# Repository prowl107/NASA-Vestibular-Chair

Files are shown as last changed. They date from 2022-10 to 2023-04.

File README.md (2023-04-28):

# NASA-Vestibular-Chair
This project is designed with the goal of restoring the NASA Vestibular Chair. The chair was actively involved in research at NASA and was recently acquired by Embry-Riddle Aeronautical University faculty. This involves restoring the basic functionality and then adding software functionality to improve the ease of use.

## Vision Statement
Our goal for the end of the spring semester (2023) is to accurately introduce a web-based interface into the external controller along with defining more accurate data acquisition over wireless connection. This consists of encoding a Raspberry Pi to allow for communication of testing procedure specifications to the microcontroller opposed to having manual input. The data acquisition will be achieved through the use of Bluetooth modules present in the microcontroller to communicate data to a host console wirelessly. If time permits, we would begin refining and updating the current design of the external controller for better usability and aesthetic. 

## Installation
```bash
git clone git@github.com:prowl107/NASA-Vestibular-Chair.git
cd NASA-Vestibular-Chair
git config user.name "User"
git config user.email "admin@example.com"
```
Alternatively, you can use a git GUI client to manage your copy of the project. 

## Usage
Open Visual Studio Code (or your text editor/IDE of choice) and then open the PlatformIO menu.
Select "Open Project" and navigate to where the repo is located on your device.
Open the PlatformIO project with the NASA-Vestibular-Chair root folder selected.
Have fun :)

## Hardware 
### Version 1 - Controller Module
| Category  | Component  |
|---|---|
| MCU  |  [Arduino Mega 2560 Rev3](https://store.arduino.cc/products/arduino-mega-2560-rev3) |
| Motor Controller  | [Pololu Simple Motor Controller G2 24v12](https://www.pololu.com/product/1365)  |
| Display  | [Standard 20x4 LCD w/ I2C](https://www.amazon.com/SunFounder-Serial-Module-Arduino-Mega2560/dp/B01GPUMP9C) |
| I/O  | SPST Momentary switch; 250k potentiometer  |
| Power Supply | USB 5v |
| Communication Interface (Receiver) | [433Mhz Receiver](https://www.amazon.com/HiLetgo-Wireless-Transmitter-Receiver-Raspberry/dp/B01DKC2EY4/ref=sr_1_3?keywords=433mhz+transmitter+and+receiver&qid=1675643344&sr=8-3) |

**NOTE:** Initially, the plan was to utilize a [Nucleo-WB55RG](https://www.st.com/en/evaluation-tools/nucleo-wb55rg.html) Development board. Due to time constraints and availability, the Arduino Mega (and Nano) were chosen due to their extensive library/peripheral support and quick prototyping capabilitiy.

### Version 1 - Patient Remote

| Category  |  Component |
|---|---|
| MCU  | [Arduno Nano R3](https://store.arduino.cc/products/arduino-nano)  |
| I/O  |  3x SPST Momentary switch |
| Power Supply   | 5v li-ion battery  |
| Communication Interface (Transmitter)  |  [433Mhz Receiver](https://www.amazon.com/HiLetgo-Wireless-Transmitter-Receiver-Raspberry/dp/B01DKC2EY4/ref=sr_1_3?keywords=433mhz+transmitter+and+receiver&qid=1675643344&sr=8-3) |

## Presentations
- [Sprint 1 Demo Presentation](https://docs.google.com/presentation/d/1b5IdnyLSNwiTLVy-gZ9E79ZbYqnyJbTD/edit?usp=sharing&ouid=115407868332019012098&rtpof=true&sd=true)
- [Sprint 2 Demo Presentation](https://docs.google.com/presentation/d/1l_CmvSCrBEOVg_VuYpDZWNs5qSBOpJvT/edit?usp=sharing&ouid=115407868332019012098&rtpof=true&sd=true)
- [Sprint 3 (End of Fall 2022) Demo Presentation](https://docs.google.com/presentation/d/1xmUZu0XUEXimdjX_mnKVwzS-KKVoy4oE/edit?usp=sharing&ouid=115407868332019012098&rtpof=true&sd=true)
- [Sprint 4 (2023) Demo Presentation](https://docs.google.com/presentation/d/1zxAWRcQLVy_wj2OVS8DIGSSmD8TUqGN_/edit?usp=sharing&ouid=115407868332019012098&rtpof=true&sd=true)
- [Sprint 5 (2023) Demo Presentation](https://docs.google.com/presentation/d/1c0bh65YAwqH6N8ktK_QlXqYoBvHQKnEx/edit?usp=sharing&ouid=115407868332019012098&rtpof=true&sd=true)
- [Final Presentation](https://docs.google.com/presentation/d/1rVZELndvWFqBjD3BzsnxDw-WVZXjoCnKRoX8ANc6Zlw/edit?usp=sharing)

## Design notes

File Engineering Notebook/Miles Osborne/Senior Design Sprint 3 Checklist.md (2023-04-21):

Web Interface Integration
Final Presentation
- New theme (ask Carson)
- System architecture
SRS updates
SDS updates
- Mostly just diagrams and software artifacts
- intended fully wireless design
Documentation:
- User manual
PCB
- Prototype with breadboards and intended power supply
- That needs to be finished post haste
3D printed enclosure
Move to fully wireless?
Fixing data logger
Test tachometer in lab on thursday/friday

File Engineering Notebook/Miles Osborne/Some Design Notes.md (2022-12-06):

# Some Design Notes

## Use Case

### Actors
- Patient
- Proctor
- Web Interface
- Chair 
- Controller module

### Responsibilities:

#### Patient Responsibilities:
- Sit in the chair
- Indicate what direction they are spinning in
- Activate soft switch

#### Proctor Responsibilities: 
- Start test sequence
- Activate soft switch
- Activate mechanical/hard switch
- Control RPM via switch

#### Web Interface Responsibilities
- Display data 
- Accept commands from I/O

#### Chair Responsibilites
	Send data
		- Accelerometer
		- Tach

#### Controller Module
- Process commands
- Read data over serial
- Send sign

### Assumptions:
- Assuming that the controller module consists of the following components:
	- Micro controller
	- Motor controller
	- 1x soft switch
	- 1x hard switch
	- 7 seg displays

### Constraints:

## State Transitions (For the chair-controller interaction)

- Powering off
	- Entry: Kill voltage to system if powered
	- Leave state once mechanical switch is pressed/depressed
	- Can go back to powering on state, once kill switch is not enabled

- Powering on
	- Entry: System initialization
	- exit: nothing
	- Do: Cycle displays 
	- Leave state once system initialization completes

- Configuring sequence
	- Nested state
	- 1. Configuring RPM
		- Leave after center pushbutton confirmation
		- Stay in state if down button is pressed 
	- 2. Configuring Time/Duration
		- Leave after centeR pushbutton confirmation
		- Go back to previous state if down button is pressed

- Waiting for proctor confirmation
	- Enter if test sequence has been set and confirmed
	- DO: Wait
	- Exit: nothing
	- Only leave state once proctor gives pushbutton confirmation
	- Go back to configuring sequence if down button is pressed

- Executing test sequence
	- Do: Send signals to chair via motor controller
	- Only enter state if arming switch is triggered

- Slowing down
	- Enter this state if soft_kill switch is pressed at any point
	- Do: Quickly bring RPM down to 0
	-

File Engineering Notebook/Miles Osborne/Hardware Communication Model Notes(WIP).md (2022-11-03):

# Hardware Communication Model Sections:
## 1. Controller Interfaces
- STM32 MCU
- Dedicated motor controller
- Dial/potentiometer to control RPM manually
- Switch to arm/comfirm ready for test
- Soft kill switch
- Buffer to store data
- 2x 7 Segment displays
- Hard kill switch
## 2. NASA Vestibular Chair
- Soft kill switch for patient
- Accelerometer
- Tach 
- Servo motor
  - Part that spins the chair
- User joystick
  
## 3. Displays and outgoing data
- Web interface

## 4. Incoming signals

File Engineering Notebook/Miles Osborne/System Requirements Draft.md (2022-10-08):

# System Requirements Draft

# Control
- The system shall allow the chair to spin upto a specified RPM
- After a specified duration set by the operator/proctor, the chair should enter a free coast state
- The system should allow the chair to spin in either clockwise or counterclockwise directions
- The system shall have a "soft" kill switch that will allow the chair to "free coast" down to 0 rpm
- The system shall have a "mechanical/hard" kill switch that will bring the chair to stop faster than the soft switch
	- By how much faster?
- The system should adjust `<parameter>` in response to the user's weight in order to maintain the desired RPM
	- Not sure what parameter needs to be adjusted yet (voltage, current, etc...)

- **HOW DOES THE RPM GET SET**?
- The system shall not exceed `<parameter>` RPM at any point during its operation

- Do not exceed 10v power consumption
- DO not exceed 4a power consumption
# Web Interface
The system shall have a web interface that allows the user/proctor to control the following

- The web interface shall allow the operator to add different test sequences 
	- **NOTE:** We don't know what constitutes a test sequence entirely yet
- The web interface shall allow the proctor to input the user's weight
- The web interface shall feature a unique button to select the test sequence
- The web interface shall have a unique button to start the selected test sequence
- The web interface shall have a text box to enter the duration of the test 
- The web interface shall display stored test sequences from a dropdown menu

# Data Acquisition
- The system shall record chair steady state (current position) of the chair
- The system shall record the rpm set by the proctor
- The system shall record the rpm that the chair is currently spinning at
	- NOTE: We will need an encoder for this
- The system shall record the time elapsed during the current test
- When the user indicates they are spinning, the system shall record the total time the user thinks they are spinning 
- When the user thinks they are spinning, the system shall record the direction they think they are spinning in 
- When the user thinks they are spinning, the system shall record the timestamps they think they are spinning for
- The system shall have the ability to export data in a human readable formate
	- Something like excel, csv, json, etc.
- The system shall have the ability to obtain positional data from an external accelerometer

# User Input/Feedback
- The system shall support user input from a bi-directional control interface
	- Button, joystick, etc.
- The system shall allow for the user to indicate what direction they are spinning in via a bi-directional control method
- The proctor cannot start a sequence or test until a separate button/switch is pressed
- The system shall record intermediate values for the direction indicated
	- x (slow, medium, fast) amount in left direction
	- x (slow, medium, fast) amount in right direction
- The user remote is wireless
- Controller has wireless recieve and transmit functionality

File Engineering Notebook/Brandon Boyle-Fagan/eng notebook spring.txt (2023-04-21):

1/11/23 - Meet with team to go over tasks and important deadlines for upcoming sprint. Compiled list of requirements to make part box container.

1/14/23 - Started modeling designs for controller box. includes power supply, arduino, motor controller, I/O

1/18/23 - Printing designs for controller box.

1/20/23 - Printing desing for controller box and assembly.

1/21/23 - Assemble first controller box. test and deug motor controller box with MAtthaeus, and Miles, as well as test first implementation of wireless remote.

1/22/23 - More 3D printing.
 
1/23/23 - Moved chair to HAL. Tested that the controller box work to power chair. assembled and soldered circuit for wireless remote.

1/26/23 - Worked with Dylan on creating a base to read the data from the tachometer 

1/27/23 - talked to Dr. Garcia about ways to Read the data from the potentiometer

2/16/23 - Talked to Dr.Pang on way to implement a PID based control system into the chair and tachometer feedback system. Worked with Dylan to Update the tachometer to use new measurement system. 

2/23/2023 - Attempted to reinstall Tach into chair.

2/27/2023 - Redesigned and printed the new casing design  for the paitent remote control.

3/3/23 - Worked in HAL to attach tachometer to chair. 

3/7/23 - Worked in HAL along with Miles and Kent to attach tachometer to chair and get RPM data from it. 

3/28/23 - class discussion to go over project

3/30/23 - met in HAL to diagnose issues with chair and tachometer 

3/31/23 - met in HAL with Miles, Kent, Matthaeus to resolve program issues for tachometer

4/4/23 - worked on redesign of controller box cad files

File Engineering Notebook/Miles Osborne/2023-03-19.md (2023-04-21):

Today is the Sunday before Spring break ends. Not much to report but did begin integration process to get Bluetooth added to the control module. Mattheus took care of most of the setup already so my role was simply making sure everything works as intended. I only made a few tweaks such as cleaning up the initialization and making sure the data logging script still works.

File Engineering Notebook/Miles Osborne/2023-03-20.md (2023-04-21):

Was able to test the Bluetooth module integration which went smoothly. The remote and control module connect seamlessly and quickly. That said I was not able to test the servo motors output. That should not be an issue since the commands sent to the control module are not hardware specific. However I was able to probe the pins with a multi meter and did confirm a non-trivial output from the pins. 

I also had time to add make the remote using the new adafruit MCUs. The circuit is much simple this time since all the communication peripherals are built-in to the board. The only tricky part was adding the circuit for powering the board. It was not technically challenging but I was hoping to find a more elegant solution. Given a current hardware and resources, the best I could do was to take one of our spare on/off switches and attach the battery leads to the pins making an on/off switch for the remote. Luckily the adafruits also have built-in battery charging as well.

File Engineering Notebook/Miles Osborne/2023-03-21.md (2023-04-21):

Today was more problematic and self inflicted. I ran into an issue where for some reason, the data logging script was not running on the original laptop we had secured for the trials. I still have no idea why this is happening but I spent all night trying to solve it to no avail. Fortunately, we have two fall back options in the form of spare laptops that Dr. French and I both have and would be willing to use for the trial that morning. 

The other issue was due to my own negligence. We have never secured the boards down so that the module would be easier to disassemble. However, this also means that electronic components can come into contact and cause shorts. While I was setting up the module, I had the foolish thought that this wouldn't be an issue because it wasn't before. Well that was a rookie mistake and I should have known better. The moment I walk into the lab, I'm told the module sparked and started smoking making it unusable for the day. It only took a few minutes for me to realize as I started debugging what likely happened. The 5V line for the Adafruit board over USB happened to tough a GND line and the rest is history. Really simple mistake and another board fried so I've learned my lesson. Silver lining though, the issue is not hard to fix and I made sure to request spare board for when something like this happens.

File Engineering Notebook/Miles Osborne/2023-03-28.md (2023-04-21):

The Bluetooth integration has gone smoothly. Thanks to Mattheus, it has been a really easy transition and the results are already showing. Our sample rate has increase significantly and we are no longer losing packets. Connecting the modules is also faster now. 

As far as changes to make, I began to improve the data logging script. Namely the data sanitation. When switching to the new board, I didn't think that the random characters that appear when reading an access amount of bytes would change. However, that is exactly what happened so I updated our data logging script to have more robust sanitation of data. 

Likewise, I made it so where detecting the Adafruit board is no longer dependent on the most recently connect COM port. This also proved to be the culprit for the previous issue for running the application on the regular laptops. To further elaborate, the data logging script would work completely fine on my laptop **without a board plugged in.** When I went to use it on one of Dr.French's laptops, it would just throw an exception and crash with no board plugged in.  I ended realizing that my laptop has a serial device built in which will have a COM port utilized. However, the other laptops don't. Pyserial will thrown an exception if it detects no open COM ports which is what was happening. My solution was to change how the board is detected. It does not change the requirement that a board must be plugged in before starting the application but instead of looking for the most recent COM port, I changed it to look for the correct USB id. This approach removes the uncertainty and guess work in looking for the device. Additionally each of our MCUs will have the exact same MCU so in case we need to replace a board in the future, we won't have to worry about updating the script to connect with the new board.

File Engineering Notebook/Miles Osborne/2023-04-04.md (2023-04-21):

Over the weekend, I took a crack at this with the document Dr. Liu sent me. I got about two thirds of the way through before my lack of matrix operations slowed down progress. The last step in the least squares approach invovled some matrix math and I didn't have the time or capacity to relearn some of the concepts. However, I did consider applying a linear regression formula to try and map when the rate of change is approximately zero. 

Today, we met in the lab and just recorded the tachometer values from the chair. Dr. Liu figured that instead of calculating it during runtime, we could do after we gather all the data. I like this approach and it gives us the ability to utilize the python math functions instead of hoping that the controller can detect the stop. On another note, I really wish our tachometer measured rate of change instead of positional values. That would make this whole process so much easier. I showed the data to Dr. Liu and Aaron later and we quickly came to the conclusion that not only is the data generated bad but the tachometer itself might be damaged. The data we got was unexpectedly noisy and for some trials, the graph flattened out at two places at the same time **which is not possible.** It also does not help that our MCU has a weird reference voltage of 3.6v instead of 3.3v. I noticed this when running a small test with a potentiometer off the 3.3v line. I would never reach the max value of the resolution. A few google searches later and I found that the culprit was the reference voltage level being 3.6v. To compensate, I tried making a voltage divider circuit off the 5v line from the USB power but did not have the exact resistors values needed. I was able to get down to about 3.67v which causes a weird roll off when approaching the max value. I wish we found these issues last month but again it is what it is. I'm thankful for Dr. Liu's quick response and assistance but I'm sorry that we let it get to this point and that we will not be able to integrate the tachometer feature. Back to the drawing board.

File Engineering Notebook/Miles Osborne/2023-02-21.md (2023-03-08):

# 2023-02-21

Lab trial went smoothly. No issues occurred but we are behind schedule slightly. The goal is still to have the new changes ready to go and the tachometer and Bluetooth features are still in development. We did bring the module back to the lab and took off the housing to ensure we were designing the right schematic. I still wish we had a better designed enclosure but oh well. My availability to work on the project for the next week or so will decrease noticeably. My involvement for the sprint is minimal but I need to also allocate time for another project I am currently leading. 

**Update:** It's very likely that us messing with the wiring this time cause the system failure on Thursday .

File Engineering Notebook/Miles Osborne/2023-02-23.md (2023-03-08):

# 2023-02-23

System critical failure,
Neither software or hardware works
Likely due to use modifying hardware the previous day
Problem because we are on the verge of integrating the new MCU
Stayed all night and soldered
Placed all components on solderable breadboard
Made a daughter board for the buttons to relieve some tension in the wires 
Also made the system compatible with the new Adafruit boards so that when we go to use the new boards, its a simple hardware swap
Debugged code at 15,000 ft :)

- During the trial today, we experienced a complete system failure. Nothing worked as expected and it was not safe to put anyone in the chair. If we set the speed to 12 it would spin slowly but any higher and it would go too fast which was not good. I also became apart of the study in a sense. I tried debugging the issue while the chamber was up to altitude which was set to 15,000ft. I definitely felt the change in pressure but I think I held it together pretty well. I can say I work well in low pressure literally. 
- Overall our system was completely broken so I took it upon myself to fix the issue after retrieving the module. The problem with this though is that, we are expecting to integrate the new boards so I couldn't just design a fix for our current microcontroller (Arudino Mega). That would just lead to more work down the line. I took inspiration from Dr. Liu's game controller PCB from CEC 320 that he recently developed but tweaked the intent of the design. I used a solderable breadboard along with female pin headers to make a mount for the new Adafruit boards. In addition to that I developed my own pin mapping scheme such that the pins of the Arduino Mega would be mapped to the corresponding Adafruit feather pins. This makes it such that when it comes time to upgrade to the new board, we only need to swap the board on the inside, not design a whole new system. 
- I also added a daughter board for the buttons to sit on so that the there would be less tension on the wires and that it would be easier to access the internals without breaking anything.
- The only downside to this approach was that it took all night to do. I was definitely here late but I felt it was necessary. The deadline to integrate the new features is next Tuesday but if the module isn't working by the next day so that there is time to test, then it severely compromises our makes Monday/Tuesday plans. It could also lead to the possibility of not being able to test which I am not willing to accept.

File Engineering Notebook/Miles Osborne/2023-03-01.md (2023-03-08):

# 2023-03-01

Suffered a communication failure with the new remote controller. Narrowed the issue down to a lose wire that somehow snapped off the model. This is likely due to the wires in the remote being thin but also using stranded wire. While the goal would be to jump straight to bluetooth, there have been issues getting that up to speed. Overall not a big issue but still disappointing. I ordered solid core wire and will replace the leads over the weekend so that this issue hopefully doesn't happen again and just in case bluetooth does not come in time.  
Dr. French gave us a deadline of Next Tuesday, March 7th to have everything done. In particular he needs the controller to be able to detect when the chair stops spinning, and resolve and communication issues.

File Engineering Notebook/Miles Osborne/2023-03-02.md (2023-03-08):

Met with Matthaeus and worked on the bluetooth connection between the Adafruit boards. I wasn't as much help here but Matthaeus had a better grip on it than I did. He was able to get it connected with the Adafruit app which is a good first step. I think I found a resource by a development team that used a board with the same bluetooth module but it didn't compile when I ported the project. Either way, my focus is shifting more towards updating our documentation before the end of the sprint and compiling the remaining tasks for the semester.

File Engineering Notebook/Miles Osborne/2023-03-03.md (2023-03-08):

Not much happened today but cam in to finish assembling the controller module and test the new wiring system from last night. After about an hour of initial setup and plugging wires in, we were able to  get setup. The trials went smoothly and technically speaking is in a better place than before!

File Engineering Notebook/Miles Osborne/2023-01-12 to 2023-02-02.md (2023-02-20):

# Intro
Instead of having dedicated entries for each day, I think it would be easier to summarize and recount the events during this period given they were targeted towards the same goal. The point of the last few days was working on the actual implementation of the system. Also, I had been full speed in order to make sure we met our deadline and didn't sleep much so some days are kind of a blur.   The trials are to begin at the end of the month and the system must be operational by then. This includes basic hardware controls, data acquisition, and interfacing with the remote device. While I would love to say that it went all to plan, there were unforeseen difficulties. 

## Software Changes
Writing the software was simple for the most part but it did take some time. I modeled the system with a typically super loop and state machine. Due to the limited time, I didn't want to write something more complex which could lead to more issues while testing. Furthermore, the device does not have extremely strict timing or request deadlines so a simple yet slightly inefficient approach is acceptable. The easiest way to remedy this is increase the clock speed of our system by acquiring a faster development board/microcontroller. We will come back to this item later. At the very least establishing the framework for the system was not hard. The only thing that I needed to do was add in the tasks during each task. Admittedly, it's not the best code but it does work and is readable. 

## Acquiring Estimate Motor Speed values
As far as implementing the code for controlling the motor, I had to do a bit of estimation which ultimately ended up being slightly wrong. We were provided a library for controlling the motor in the chair but the actual implementation designates a speed value on a range of -3200 to 3200 where -3200 is full speed in one direction and 3200 is full speed in the other.  However, full speed isn't a good metric to go by and fails to validate our requirement that we do not speed faster than 19 rpm per minute. Since we only need to spin in one direction and took some samples of the motor at different speed settings. I initially tested it at 25%, 50%, 75%, and 100% speed. For 60 seconds, I counted the number of revolutions and got a rough estimate of the speed. Apart from the human error introduced I found that the values were roughly linear. 

Half speed: 17.5 revolutions per minute
Full speed: ~42 (41.75ish) revolutions per minute
75% speed: 29.5 revolutions per minute
25% speed: 3.75 rpm

This feature made it easy to map the potentiometer value to the RPM value that the proctor wants to set. I added a higher resistance potentiometer and 0.1μF capacitor to get rid of much of the analog noise and sensitivity. 

**NOTE**: On recount and looking back at data files, I found that I did this on **Saturday January 21st** 

The problem with this method however, is that it assumes a "best case" scenario. There was no load or person sitting in the chair. Essentially, it takes less power for it spin at 14 rpm if there is no one sitting in the chair. The opposite is also true where it takes more power for it to spin at the set speed if the person or object is heavier. However, our code does not currently adjust to the person's weight. For our system, a heavier load will only cause the person to spin at a slower than desired speed. We were aware of this phenomenon for awhile but saw it in person after we initially moved the chair to the high altitude lab. For example, I weigh roughly 130 lbs (I'm the lightest person on our team) but Kent who is closer to 200lbs would not spin at the same rate if the speed setting were the same for the both of us. Dr. French has not expressed to much concern over this for now but we will likely have to return to this after Brandon can successfully analyze and interpret data from the tachometer

# Remote Connectivity
This is where many of the issues stem from and is the weakest part of our project. Because we need to source data from the person in the chair who is spinning around, we can't rely on wired communication protocols. The original plan was to use Bluetooth but Brandon had in foresight, put 433MHZ radio transceivers/receivers on the budget. Initially this seemed like a good thing give the lack of time we had but ultimately it because the biggest pain of this entire project partially because I spent the most time debugging it. Furthermore, the communication method was only one way, not bi-directional which can come back to bite us later when we need to sync data between modules. The code for the system was simple to implement but after isolated tests that we did it went all downhill. When we put it in the 3D printed enclosure (which wasn't very accommodating to begin with) data was being lost on multiple occasions. I switched microcontrollers/development boards and soldererd the whole thing over again for it to work one hour and then not at all the next. I don't remember why but I somehow had the intuition to isolate the possibility that it was a connection issue. To isolate, I desoldered the horizontal pin headers and then directly soldered wires to the board. We also added another transmitter to the remote modules which seem to prevented the random loss of packets but I'm not particularly convinced. Still, as long as it works, then that is all that matters but there is a unanimous agreement that these modules are going to be replaced during the next sprint. 

## New Boards and Bluetooth
On **January 26**, I did have time to research into wireless communication protocols. I had never done too much work involving telemetry so this was an interesting experience. I started looking into the specifications of the Bluetooth protocol and found that there are two types of Bluetooth connections: classic and low energy (BLE, LE). I don't know all the specifics between the two but the capabilities of both will suffice for our project although it seems like BLE is more common currently. One thing I did make sure of is the directionality of the data transfer. Thankfully, Bluetooth is bi-directional where the host/master or slave can transmit and receive data. The only problem is time stamping/syncing the data between modules. Luckily, there is a reference book in the library titled *The Embedded Systems Handbook* by Richard Zurawski which has a section on time syncing for wireless communication protocols. The book is somewhat old so there may also be newer ways of implementing that aspect of it. 

As stated above, the original plan was to use the bluetooth protocol but more specifically we were going to use the bluetooth module on the Nucleo WB55RG development board. The STM development boards offer a more traditional embedded software/systems environment which gives us alot of control over our project, more than we will ever need. While I am partial to nucleo and STM boards, I decided to look for alternatives. This is for a few reasons:
1. I am the only one our project (apart from Aaron who isn't a member) who has experience with embedded systems and software greater than just an Arduino. 
2. I don't want to introduce complexity into our system just to give myself a challenge especially when people are depending on this device to work. 
3. Our existing code is written using the Arduino framework (due to a hardware failure which I caused breaking one of our original boards)

With that said I needed a board that was compatible with the Arduino framework, compatible with our current system and its components, has a small footprint, preferably had a wireless communication peripheral built in or easily integrates with one, and is preferably faster. After a little bit of searching I stumbled across the a few boards based on the ESP32 MCU and a Cortex M4F. Most notable were the [Feather S3](https://esp32s3.com/feathers3.html) , [Adafruit HUZZAH32](https://www.adafruit.com/product/3405), and the [Adafruit Feather nRF52840 Express](https://www.adafruit.com/product/4062). While the Feather S3 and Huzzah32 were more powerful and seemed to have the greater feature set, I opted to go for the Adafruit Feather nRF52840 express. In embedded software/system development, a very easy mistake to make is to go with the option that has the best of x attribute. For instance the fastest processor or clock speed. That is a terrible design and decision making philosophy for this particular area because you often can introduce more issues by following that rule. The Feather S3 was the newest if memory serves but the least documented. If any issues were to occur (which they probably would), then we would effectively be alone in solving them which then means I'm pretty much alone solving them. The Huzzah32 had the most powerful processor and the best specs but was still under development and was not entirely stable. That last bit is especially important as it pertains to compatibility with the rest of our system. That left the adafruit feather nRF52840 which while the weakest, was still 4 times stronger than our Arduino Mega that we were currently using and well documented to support the Arduino framework. It had a dedicated bluetooth module built in supporting both classic and LE modes and was not terribly expensive either. I think it is cheaper than a genuine Arduino Mega which is surprising.

## Feedback from High Altitude Trials
We began the trials on January 24th which did not start off amazing. The biggest issue being the remote connectivity. Data was being lost on multiple runs for one reason or the other. That said, the actual hardware control of the chair worked correctly. I ended up writing a simple data acquisition script using Python & Pyserial to log the data on one of Dr. French's laptops as a csv file which worked well. 

Two students have been responsible for operating our system during the trials thus far, Kalen and Phillip. I've been communicating with them to try to make the system easier to use. I understand how the system works but what an engineer perceives as easy may not appear that way to someone else. Both of them expressed the need for more visual indicators and feedback when certain events were occurring or complete such as when the remote is connected or the data has successfully been stored. I thought this was fair so I  made some adjustments to the program to better indicate the state of the system. Otherwise, I have been present for all the trials thus far providing tech support (and moral support) when operating the chair. While I cannot be inside the chamber during the experiment, we can communicate still since the chamber walls are clear. We have been using hand gestures and writing notes when there are any issues during the trial. It's not every day that you can see a high altitude indoctrination tests and its great to see our system being used.

Outside of the trials I have been involved in some discussion to make sense of the data collected. Towards the end of the month the data seemed to be getting more accurate, which is leading to some contradiction from the visual results recorded by the observers standing by during the trials. I can't say what the cause of the discrepancy is yet but I figured the best way is to gather more reliable data by improving our hardware. 

In a similar vein, Dr. French asked that we record the time when the chair reaches a complete stop. We can't do this given our current capability since Brandon is still working with the tachometer. However, we can have the proctor mark the timestamp by pressing one of the buttons on the controller module. Given the recent changes, I need to find time to update our documentation to include this new additions. 

A common complain however are the quality of the enclosure for the remote and the buttons we used. The enclosure we build is too shallow for all our hardware without tightly wrapping all of the wires. It also does not close completely and some of the wires are exposed which is not a pretty sight. The buttons we used are without a doubt cheap and have to be completed pressed in order to record a value. There might also be some misreads we those as well. 

## Final Words
As the sprint comes to an end, I can say that we achieved our objective. That said, I found it kinda unfair that I did most of the work. Yes the other members contributed but I can confidently say that I have spend the most time working on this project both from a management and technical perspective. Furthermore, I am the only member at the time of writing who has showed up to the high altitude lab trials. This may be due to schedule conflicts but its evident that I am putting in the most effort regardless but that has its consequences. I can understand additional responsibility for being the scrum master and what is effectively the team lead but at a certain point it is too much. I ended up having to cancel the February launch for a project that I am leading which felt awful. For the next sprint, I do plan on making it more dependent on the other member's contributions. This project cannot live or die based on the effort of one person.

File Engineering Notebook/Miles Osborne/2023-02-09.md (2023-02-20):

Met in the Lab to discuss sprint goals
Also began assigning tasks
Ordered higher quality buttons

Today was a fairly short meeting. Simply put we met to discuss our current sprints goals and began to assign tasks. Stupidly, I missed the chance to do a sprint retrospective with everyone but did express my dissatisfaction with the spread of work from the last sprint.

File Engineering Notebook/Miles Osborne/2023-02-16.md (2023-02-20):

Helped with the high altitude trial
Tried to investigate where the ambiguity might be coming from 
Went smoothly overall
Met in lab to discuss tasks and make sure that everyone knows what they're doing
Need to update task board still

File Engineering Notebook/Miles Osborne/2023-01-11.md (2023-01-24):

# 2023-03-11

## Semester Goals:
- Finish the controller module, both the software and hardware
- Come up with a better names for everything
- Complete the web interface
- Investigate simulation/HITL testing
- Flush out the interface
- Further define web interface (and user interface) requirements
- Streamline the project setup 
- Create a user manual and SOP for operating the device
- PCB for the chair
- Interface the controll module with the web interface
- Refine the actual chair setup and power configuration
- Actually come up with good design
- Incorporating the wireless joystick

## Who does what:
- Noah:
- Dylan:
- Mattheus:
- Brandon:
- Kent:
- Miles:

## What needs to be done (explicit tasks/areas)
### Some explicit tasks ideas
- System power configuration
  - **Both the chair and the controller alongside any other peripherals**

- Finishing the functionality of the controller
- Ordering more MCUs
- Determining if we really need the heating element simulation and if so **getting on top of it immediately**
- Giving the controller a proper enclosure
  - This includes designing and fabricating a PCB and or whatever physical items needed for proper and secure mounting
    - Ethernet?
  - Installing the ethernet ports on the chair and controller module
- Integrating the joystick
- Maintaining requirements and design aspect (we might need a dedicated documentation person) 
- Organizing the github and defining a single location for photos and external documentation
- Web interface 

### Areas
- Documentation & Management 
  - SRS
  - SDS
  - SOP
  - User manual

- Embedded software (3 people)
  - Joystick
  - Controller module

- Web interface (1 people)
  - Define actual interface

- Chair/system power & setup

- Simulations
  - Completing the hardware
  - Creating or modifying the software environment
  - Documenting deviation from typical software setup

## Additional Notes:
- Assuming that the webi interface will be controlled via mouse & keyboard

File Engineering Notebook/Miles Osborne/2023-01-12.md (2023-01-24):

# 2023-01-12

## Items to get the chair operational
### Software
- State machine
- Potentiometer inputs working
  - 1 for speed
  - 1 for time
- Button inputs working
- Proper output to the chair (not dependent on chat)
- Output to 7 segment display 
- Soft stop switch for patient

### Hardware/Physical Mounting
- Measurements
- Printing
- Mounting

### Power
- USB connected/powered for chair
- Dedicated 12v line for chair
  - Mechanical stop

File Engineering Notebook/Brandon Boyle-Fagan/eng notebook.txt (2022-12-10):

SEPT 16 2022 14:40- The group went to the lab with the vestibular chair to attempt to take off the base plate and get a look at the inside of the chair. 
				I was able to remove one of the screws, but the other drew heavy difficulty.
        In the meanttime, we removed the face plate of the wire ports to get a look inside the chair.
        After some time, Dr. French returned with the correct wrench to remove the screw on the base plate of the chair.

SEPT 20 2022 14:30 - Today the group went to Dr. French's lab to get some more analysis of the chair done. 
  Matthaeus, Kent, and I analyzed the connection ports that Dr. French had purchased ahead of time in an attempt to match one to the existing ports on the chair.
  Matthaeus and I came to the conclusion that one of them could work, but would need to be adjusted to fit correctly, or a completely new set of ports would need to be purchased.

OCT 27 2022 - we were able to test the motor controller functions using a 6V stepper motor and a battery.  

NOV 1 2022 14:30 - Miles and I soldered the connectors onto the motor contorller. Kent, Matthaeus and I were able to get the chair wired and the program running to test the movement of the chair with our purchased motor controller. 

NOV 8 2022 14:30 - created a high level fist schematic of connections for chair, and various controllers. 

NOV 29 2022 - while testing the speed controls of the motor controller and chair, Created table to relate power output (Volts, current) to the motor output as a percenetage and in the future an RPM Value. 

DEC 1 2022  - dissassembled built in tachometer/potentiometer and created arduino script to read output values. next step will be to get algorithm to convert rate of change in pot values to RPM speed 

DEC 6 2020 - created circuit and arduinol script to control chair motor using potentiometer

DEC 8 2022 - Researching ways to get an RPM output from built in tachometer values

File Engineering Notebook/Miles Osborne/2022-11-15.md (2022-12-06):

Today was a bit slower. I spent time going over our design and thinking of ways to either improve it or flush it out. Talking with Dr. French and Dr. Liu have led to our requirements changing a bit and it seems our design as well. This week is especially busy due to another project but I don't want to fall to far behind. Seeing as we established that we can spin the chair with the motor controller, the next step to tackle would be to start writing the software for the controller module. Unfortunately, none of us are free in the immediate future to get the going.

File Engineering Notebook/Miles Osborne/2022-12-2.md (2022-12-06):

# 2022-12-2

My objective for the day was to start working on the software for the controller module. Clearly, I wasn't paying attention to deadlines and thought we would have until final's week to iron everything out. I've been busy with other items and haven't had the chance to sit down with the others and start writing the software. Today's session didn't fair much better. We were able to get the development environment set up quickly. However, uploading actual code to the target was difficult. No matter what we tweaked, our embedded target seemed to be ignoring the flashed program. All we were attempting to do was trigger the onboard LEDs but it wouldn't work. We are using the Arduino framework to speed up development/prototyping which is supported on the Nucleo-WB55RG. Still, it did not want to work at all. Even with four of us working on it, nothing we did would solve the issue. We eventually, had to concede for the day but we will return tomorrow to pick up where we left off.

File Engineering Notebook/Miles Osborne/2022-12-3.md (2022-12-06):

This is a continuation from the previous day where we tried to get code running on the Nucleo boards. It went much smoother than yesterday. What is weird though is that no changes were made between the code today and yesterday. It magically worked all of suddenly. Anyways, our trial was simply to trigger the on-board LEDs and then see if we could read in a value from the analog pins. We were able to achieve both objectives which makes me more optimistic about developing the code for the controller module. That said, I wish we had a little more time this sprint. The next step is writing a simple control loop for the demo test. My idea is to come up with a simple state machine to try and simulate how the proctor will use the device. Simple in concept but it hardly is ever that straightforward.

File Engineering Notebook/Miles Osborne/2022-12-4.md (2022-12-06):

# 2022-12-4

I spent most of the day working on the controller code more. My aim was to implement a simple state machine for the system but I don't feel amazing about it. There are a couple of blank spots left since the functionality of the motor controller over serial has not been tested yet. Upside though, the seven segment displays, potentiometer, and nucleo board all work together almost seamlessly. While the Nucleo-WB55RG supports using the Arduino framework, having to constantly check the pin mapping scheme has been tedious and annoying. While it works for a demo script, it might be worth serious consideration to switch to exclusively the STM32 HAL library or another framework. The downside is that we would then be responsible for developing all the libraries and interfaces for peripherals. Embedded C is a paradigm not everyone has a lot of experience in.

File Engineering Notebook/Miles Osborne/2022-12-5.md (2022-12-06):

# 2022-12-5

Today's objective was finishing up the controller module to get a simple hardware based controller. I ended up coming across example code for how to use the motor controller within the Arduino framework. I had already verified that the other modules worked with the nucleo board but the servo motor was the remaining piece. I was a little fearful of having to write I2C drivers in such a short time frame but luckily my fears have been averted. This framework along with the user guide gives good insight into sending commands to the motor controller over I2C. 

```cpp
`#include <Wire.h>`  
   
`const` `uint8_t smcDeviceNumber = 13;`  
   
`// Required to allow motors to move.`  
`// Must be called when controller restarts and after any error.`  
`void` `exitSafeStart()`  
`{`  
  `Wire.beginTransmission(smcDeviceNumber);`  
  `Wire.write(0x83);`  `// Exit safe start`  
  `Wire.endTransmission();`  
`}`  
   
`void` `setMotorSpeed(int16_t speed)`  
`{`  
  `uint8_t cmd = 0x85;`  `// Motor forward`  
  `if` `(speed < 0)`  
  `{`  
    `cmd = 0x86;`  `// Motor reverse`  
    `speed = -speed;`  
  `}`  
  `Wire.beginTransmission(smcDeviceNumber);`  
  `Wire.write(cmd);`  
  `Wire.write(speed & 0x1F);`  
  `Wire.write(speed >> 5 & 0x7F);`  
  `Wire.endTransmission();`  
`}`  
   
`uint16_t readUpTime()`  
`{`  
  `Wire.beginTransmission(smcDeviceNumber);`  
  `Wire.write(0xA1);`  `// Command: Get variable`  
  `Wire.write(28);`    `// Variable ID: Up time (low)`  
  `Wire.endTransmission();`  
  `Wire.requestFrom(smcDeviceNumber, (uint8_t)2);`  
  `uint16_t upTime = Wire.read();`  
  `upTime |= Wire.read() << 8;`  
  `return` `upTime;`  
`}`  
   
`void` `setup()`  
`{`  
  `Wire.begin();`  
  `exitSafeStart();`  
`}`  
   
`void` `loop()`  
`{`  
  `// Read the up time from the controller and send it to`  
  `// the serial monitor.`  
  `uint16_t upTime = readUpTime();`  
  `Serial.print(F(``"Up time: "``));`  
  `Serial.println(upTime);`  
   
  `setMotorSpeed(3200);`   `// full-speed forward`  
  `delay(1000);`  
  `setMotorSpeed(-3200);`  `// full-speed reverse`  
  `delay(1000);`  
`}`
```

However, I made a really simple and rookie mistake when trying the example code on the Nucleo board. While I did follow the wiring diagram, I completely forget to tie everything to a common ground (GND). I foolishly ended up damaging one of our nucleo boards and one of my own microcontrollers. This was completely my fault since the whole incident could have been avoided if I paid a little more attention. I later implemented the setup correctly after re-soldering all the pins and making sure all mechanical connections were solid. I need to retest the setup using the spare Nucleo board but for the time being an Arduino mega will suffice for a development board.

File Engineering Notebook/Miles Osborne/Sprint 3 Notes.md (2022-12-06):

# Sprint 3 Notes

### Task Ideas
### Web interface
- Develop more robust interface
- Develop example user interfaces
- Create a demo test script

### Physical Controller/Enclosure
- Get components
- Integrate mechanical switch
- Wiring diagram/schematic
- Make the temporary enclosure neat

### Embedded Software
- Develop develop and test demo script
- Investigate SDK for motor controller
- Integrate seven seg display
- Integrate potentiometers/rotary encoders
- Verify commands sent to motor controllers

Simulation: 
- Get Heating element
- Trial runs with chair (Start next week)
- Get sample data
### Misc
- Get Kent reimbursed

28th 
- Gradually ramp up to speed by 1.15 degrees per second (if possible)
- 19.8 ~ 20 rpm
- 

**Mechanical switch only kills power to chair**

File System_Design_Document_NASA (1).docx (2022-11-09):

System Design Document

For

# NASA Vestibular Chair

Team member:

Brandon Boyle-Fagan

Matthaeus Gebauer

Miles Osborne

Dylan Prothro

Noah Reid

Kent Wilson

Version/Author | Date
1 | 10/6/2022
1.1 | 10/27/2022
1.2 | 11/8/22

# TABLE OF cONTENT

# System Design Document

# 1 INTRODUCTION

## 1.1 Purpose and Scope

The goal of the NASA Vestibular Chair project is to restore the basic hardware functionality of a rotating chair that was acquired by Embry-Riddle that was used by NASA to test the human vestibular system and provide it with a new controller. This consists of ensuring the system can reach a specified RPM, hold that specified RPM for a set duration and allow the servos to gradually slow down to idle. Once the initial controller is created and able to provide intended the functionality to the vestibular char, we will begin integrating more modern software and hardware tools to improve the "quality of life" features of the chair. This includes a web interface, custom test profiles/sequences, and the ability to read and store sensor data from the chair.

## 1.2 Project Executive Summary

This section provides an overview of the NASA Vestibular Chair project from a macro perspective, showing the framework with which the system design was conceived.

### 1.2.1 System Overview

The NASA Vestibular Chair system consists of the hardware component of the chair itself, which is connected to a controller composed of a motor controller and other components to be able to handle digital and analog inputs for the chair motor. An additional web interface is planned to be added to the controller to allow for a more precise measurement of the input for the chair. The hardware components of the chair consist of a tachometer, motor, and the actual chair itself as well as some other pins set up for other once-used analog measurements. Figure 1 listed below, details a use case diagram of the NASA Vestibular chair system.

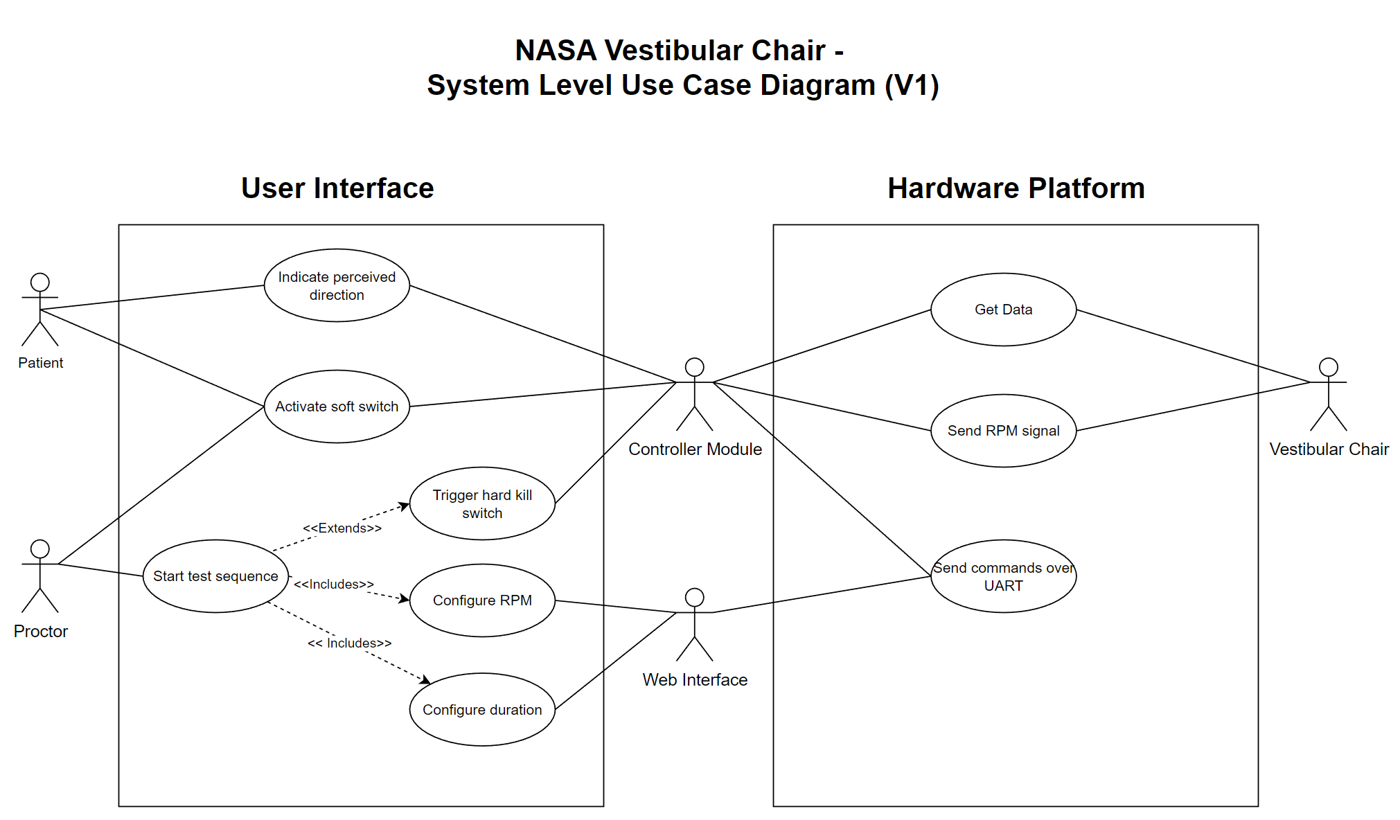
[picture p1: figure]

Figure 1: Use Case Diagram for NASA Vestibular Chair

### 1.2.2 Design Constraints

The development team plans to keep as much of the original internal hardware of the chair as possible. With this in mind, one of the major constraints in design of the controller of the chair and its interface is to have the new components work with the older technology present in the chair. Another constraint comes from the speed the chair is going to be allowed to move. The chair needs to be set to not move faster than a rotation of 100 degrees per second, and with that constraint, the controller needs to be programmed to not allow an input of voltage that would cause a rotational speed higher than that. The controller also needs to have a mechanical kill switch, meaning it needs to be connected to the power being sent to the chair via the controller to be able to shut off power being sent to the chair if necessary.

### 1.2.3 Future Contingencies

Future contingencies include the inclusion of a digital part of the controller to account for any analog issues, with the intent to keep an analog and digital component to control the inputs of the chair. Another contingency comes from the alternative components that the team researched in case the planned components are not available or do not work for the direction of the project. This includes researching two different types of motor controllers, Pololu - High-Power Simple Motor Controller G2 24v12 and Pololu - RoboClaw 2x15A Motor Controller (V5E). While the G2 is the preferred motor controller for the system, the functionality of the RoboClaw was investigated and was determined to be able to be used in place of the G2 if issues arise such as lack of power output or component damage. The inclusion of a mechanical kill switch is a contingency to avoid having the chair spin out of control if too high of a voltage is supplied to the device.

## 1.3 Document Organization

This System Design Document is organized into six sections. The introduction section explains the basics of the design, followed by the document going over the system architecture, the human-machine interface, the detailed design, and external interfaces.

## 1.4 Project References

No references at this time.

# 1 SYSTEM ARCHITECTURE

The system uses an interface of hardware and software to control the movement of the NASA Vestibular Chair, as well as measure its speed and other readings.

## 1.1 System Hardware Architecture

The composition of the hardware is represented by

- NASA chair
  - The NASA chair consists of inner hardware such as its motor and sensors already installed in the device such as a tachometer, which will be used to measure the speed of the chair during operation. The plan is to keep the sensors that are already in the chair if they are still usable, however it is also on the table to replace them if necessary.
- Controller Module
  - The controller module will consist of a dedicated microcontroller, internal motor controller, and physical I/O such as a potentiometer and switches to quickly control the state and execution of the system. The current plan is to use the Nucleo-WB55RG microcontroller to control the system and interface with the G2 24v12 motor controller to achieve the desired functionality. The motor controller has, upon initial inspection, seemed like one of the best choices for the overall scope of the project.
- Wireless bi-directional input
  - This module is a recent addition to the system. Part of the core functionality of the NASA vestibular chair is to allow the user to indicate what direction they believe to be spinning in. Due to the physical constraints of the chair spinning, we must use a wireless input to give the user this feature. However, instead of buying an off-the-shelf component, there is the argument for fabricating one. At the current state of development, this is not a high priority and this topic will be expanded in a later revision.

## 1.2 System Software Architecture

The software is planned to be an embedded systems project mostly developed using C++. Since the microcontroller selected is the Nucleo-WB55RG, the STM32 HAL library is available to use and officially supported. Other frameworks can be utilized such as the libopencm3 framework. Due to the urgency of the project, writing drivers for each component of the project is not feasible and would artificially and unnecessarily increase the difficulty of the project.

The Nucleo-WB55RG is the core of the controller module and will interface with several peripherals including the motor controller and two seven-segment displays. Both of these peripherals can be controlled via the I2C protocol which makes the software written easier to implement and maintain.

The second aspect of the system is the web interface which gives the proctor more options as it relates to creating test sequences and displaying data during the test. Data is read from the chair via the analog pins and then temporarily stored in a buffer. The data is then sent over UART to the web interface and displayed on the host computer. Likewise, when the proctor wants to actuate the chair, they will use the web interface to configure the test. When ready, the test sequence information will be sent via commands over UART and then processed by the Nucleo microcontroller. The system shall then begin to follow the sequence of events as indicated by the proctor’s designated test sequence.

A state transition chart for the System based excluding the web interface is listed below. The web interface was excluded at this time to focus on the current priority of more robust mechanical control. However, when the web interface and accompanying features are introduced, the state transition chart should be very similar.

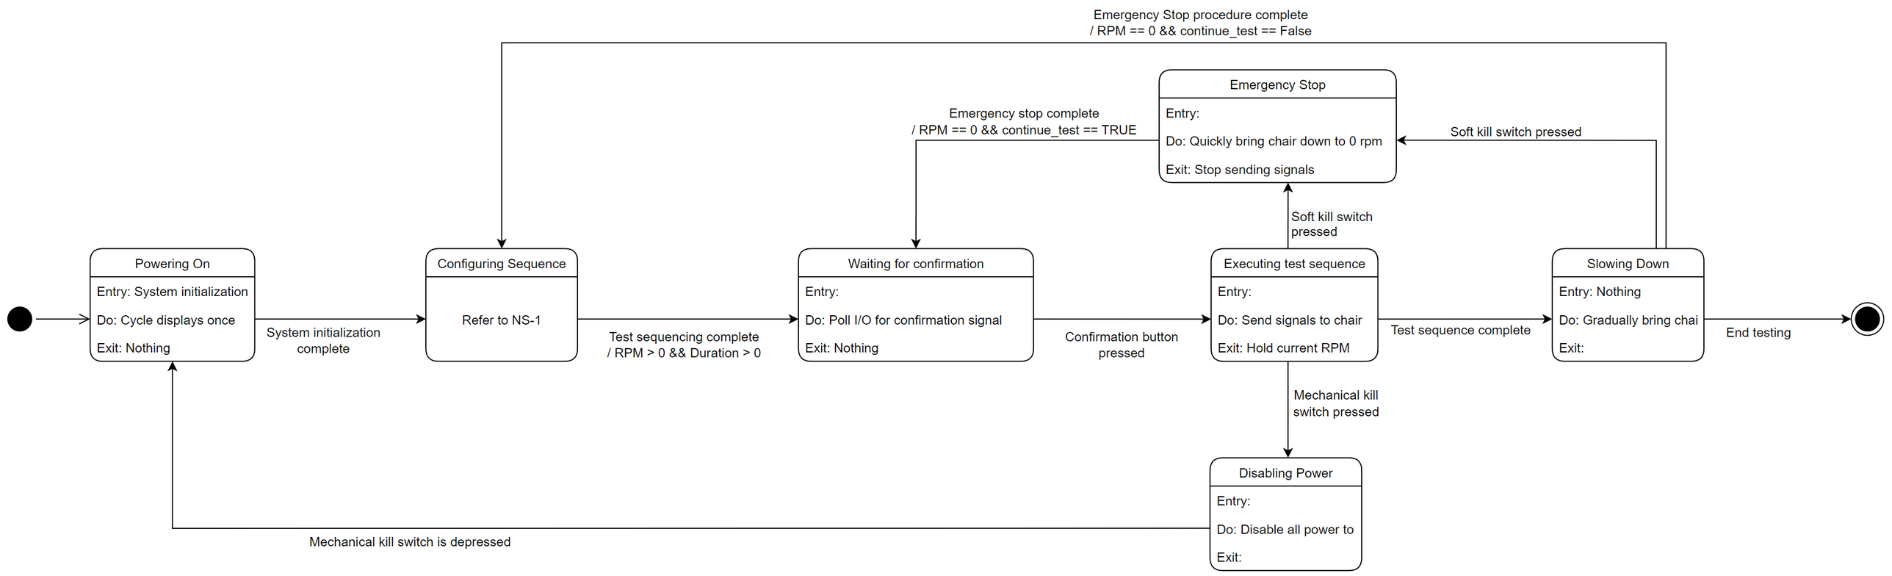
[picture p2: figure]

Figure 2: State Transition Chart for NASA Vestibular Chair

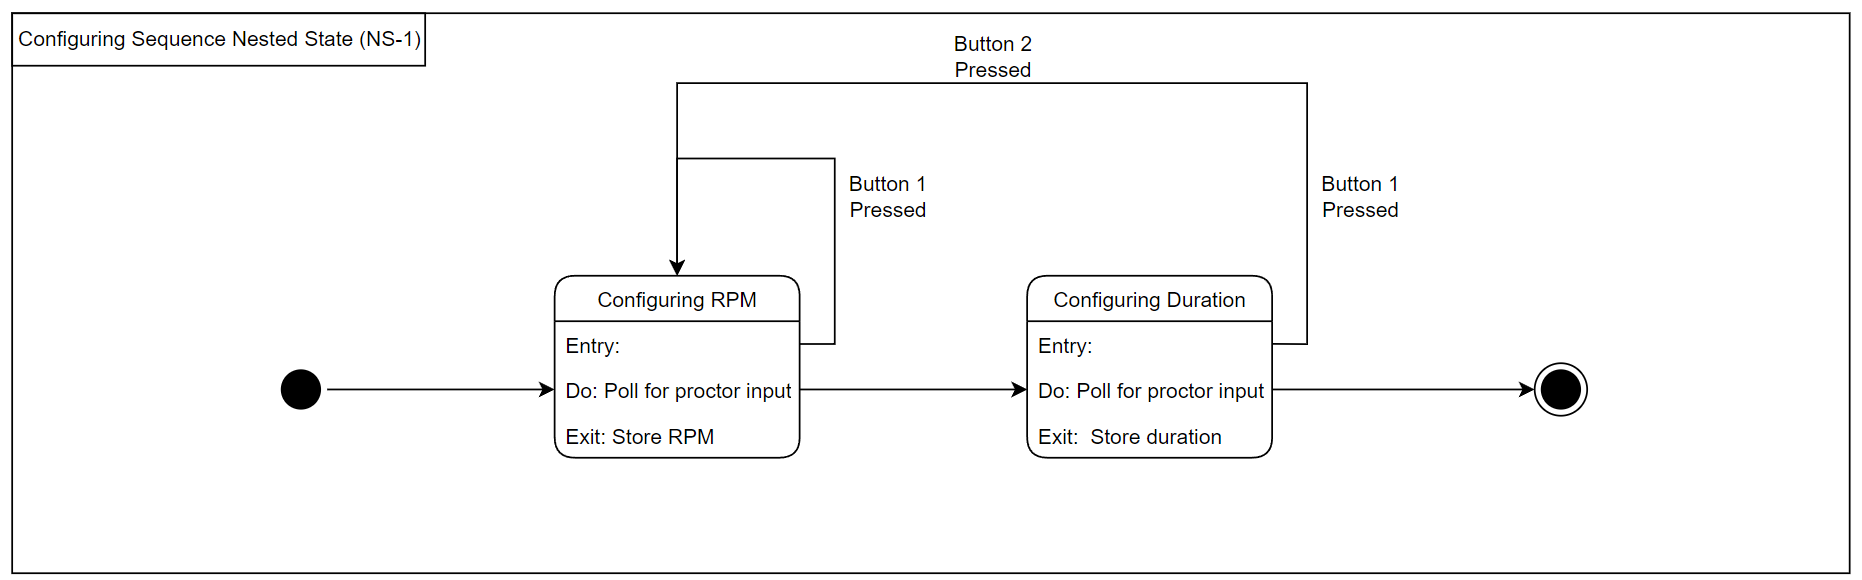
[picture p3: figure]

Figure 2.1: Nested State 1 for State Transition Chart (NS-1)

## 1.3 Internal Communications Architecture

In the NASA Vestibular Chair System, the main communication channels happen over UART from sending and receiving commands from the web interface and processing digital signals from the controller module I/O. Additionally, I2C will be utilized by the Nucleo microcontroller to interface with the motor controller and the seven-segment displays. Lastly, Bluetooth will be utilized to receive data from the wireless input device indicating what direction the user believes they are spinning in. This is feasible because the Nucleo-WB55RG has a built-in Bluetooth module. Due to the recent changes in the communication architecture, a diagram detailing the inter-communication between components is not ready at this time but will be included in the next revision of this document.

Figure 3 listed below is a simple data flow diagram, detailing the critical piece of information being transferred from components.To make the diagram more simple, the controller module is assumed to include all required electronics including the Nucleo Microcontroller, G2 motor controller, seven segment leds, switches, and the potentiometer.

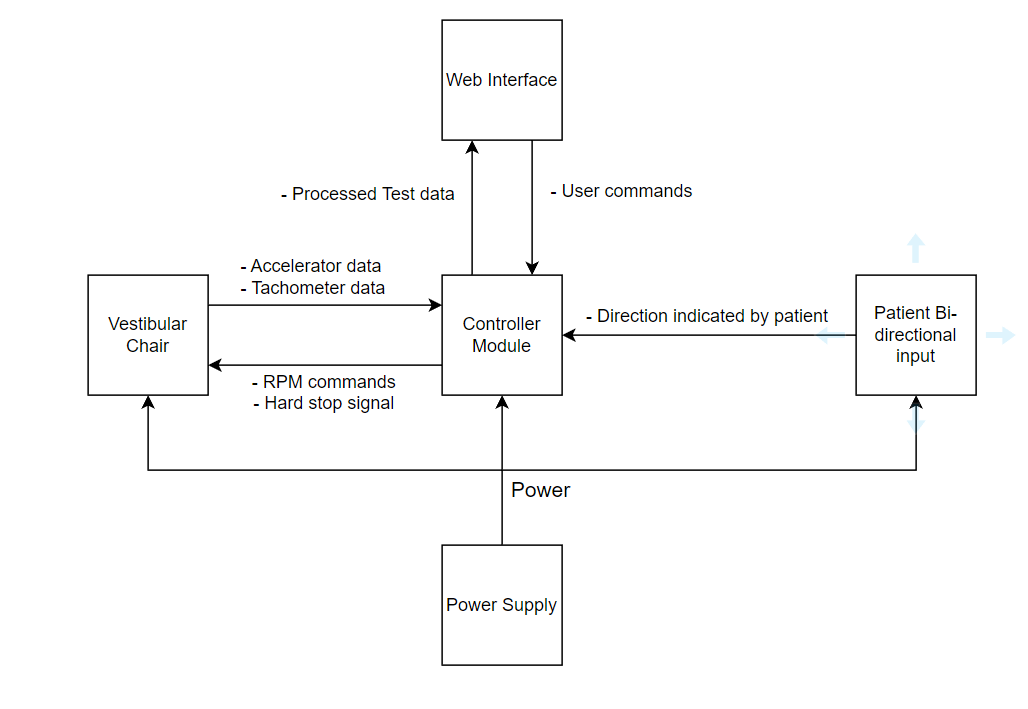
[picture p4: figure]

Figure 3: Level 0 Data Flow Diagram for NASA Vestibular Chair System

# 2 HUMAN-MACHINE INTERFACE

Human input will be necessary for the system as the input for the chair is needed to increase its voltage and by extension its speed. This interaction will cause the user to be able to adjust the chair’s speed gradually through the controller device.

## 2.1 Inputs

The inputs of the system will be given from the controller to the chair to allow movement of the chair or set up of testing cases for the voltage to be applied without needing to be adjusted by the user. These inputs are user-generated, as the individual in control of the device sets the voltage that the chair is being given. The sensors used will also count as input, including things such as the tachometer and accelerometer. Another input will come from the individual sitting in the chair, as they will be able to send data indicating the direction, they believe they are spinning in.

## 2.2 Outputs

The output response from the chair should be the tachometer reading to feed into the controller to control the speed via its feedback. This will allow the system to avoid reaching a speed that outpaces the scope of the controller. The other output is that given from the chair itself, which is its actual rotation given the input voltage supplied by the controller. The feedback from the chair should also be able to communicate the direction it is rotating to the controller.

# 3 DETAILED DESIGN

This section contains detailed information about the hardware and software design of the system

## 3.1 Hardware Detailed Design

The system is centered around the Nucleo-WB55RG microcontroller. This component will perform the following roles at a minimum:

1. Accept user input from the proctor
2. Perform data acquisition at a sufficient sampling rate
3. Process commands sent via UART
4. Send data to peripherals through I2C
5. Process commands via Bluetooth from wireless bi-directional input
6. Send data to the web interface via UART
7. Control the vestibular chair’s RPM via commands sent to the motor controller.

Figures 4, 5, and 6 are a simplified overview of the hardware and components present in the system. Note, that these diagrams do not document the internal communication between each module.

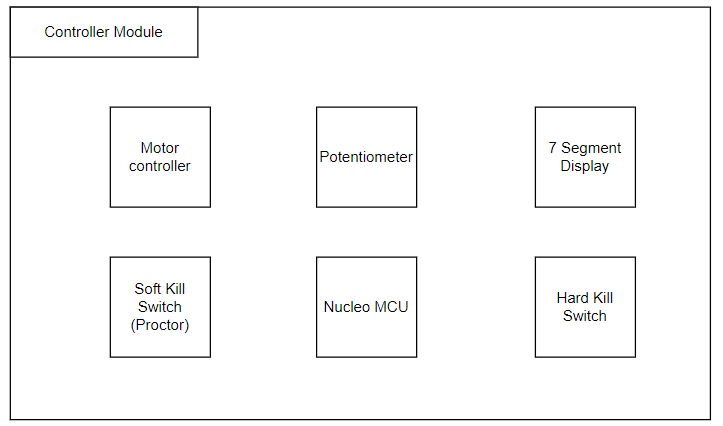
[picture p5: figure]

Figure 4: Simplified overview of NASA Vestibular Chair Controller Module

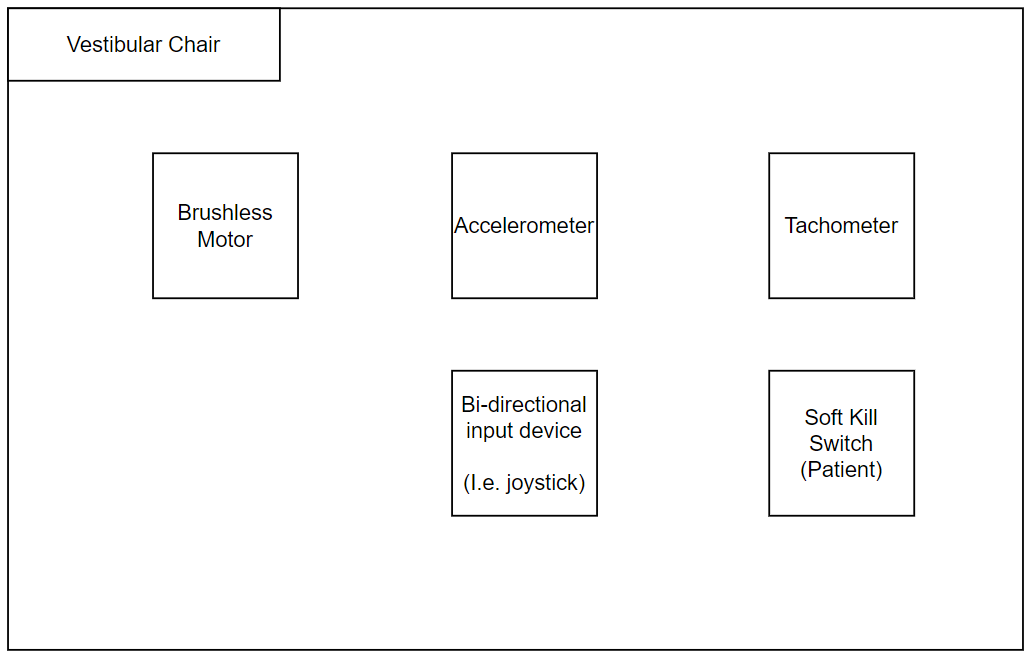
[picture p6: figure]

Figure 5: Overview of NASA Vestibular Chair Components

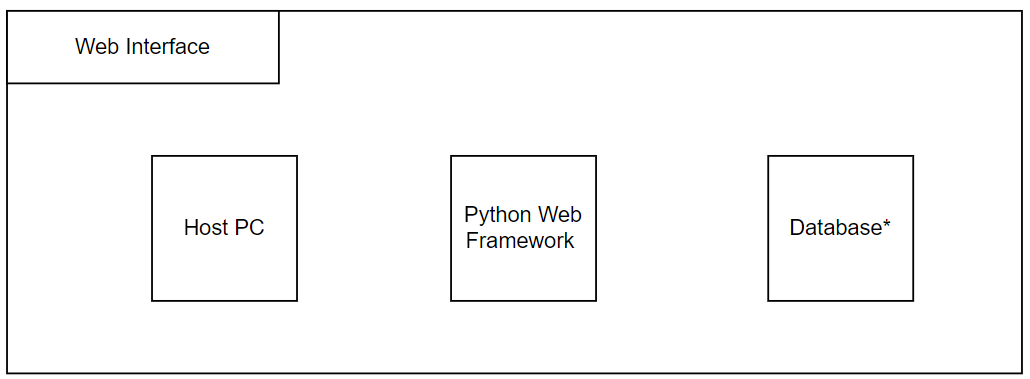
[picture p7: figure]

Figure 6: Overview of Web Interface Components

## 3.2 Software Detailed Design

A software module is the lowest level of design granularity in the system. Depending on the software development approach, there may be one or more modules per system. This section should provide enough detailed information about logic and data necessary to completely write source code for all modules in the system (and/or integrate COTS software programs).

If there are many modules or if the module documentation is extensive, place it in an appendix or reference a separate document. Add additional diagrams and information, if necessary, to describe each module, its functionality, and its hierarchy. Industry-standard module specification practices should be followed. Include the following information in the detailed module designs:

- A narrative description of each module, its function(s), the conditions under which it is used (called or scheduled for execution), its overall processing, logic, interfaces to other modules, interfaces to external systems, security requirements, etc.; explain any algorithms used by the module in detail
- For COTS packages, specify any call routines or bridging programs to integrate the package with the system and/or other COTS packages (for example, Dynamic Link Libraries)
- Data elements, record structures, and file structures associated with module input and output
- Graphical representation of the module processing, logic, flow of control, and algorithms, using an accepted diagramming approach (for example, structure charts, action diagrams, flowcharts, etc.)
- Data entry and data output graphics; define or reference associated data elements; if the project is large and complex or if the detailed module designs will be incorporated into a separate document, then it may be appropriate to repeat the screen information in this section
- Report layout

# 4 EXTERNAL INTERFACES

The current external interface is the idea/plan to add a web based component for the controller. This is not currently within the scope of the basics of the system; however, it is something that is planned to be attempted time permitting.

## 4.1 Interface Architecture

In this section, describe the interface(s) between the system being developed and other systems; for example, batch transfers, queries, etc. Include the interface architecture(s) being implemented, such as wide area networks, gateways, etc. Provide a diagram depicting the communications path(s) between this system and each of the other systems, which should map to the context diagrams in Section 1.2.1. If appropriate, use subsections to address each interface being implemented.

## 4.2 Interface Detailed Design

For each system that provides information exchange with the system under development, there is a requirement for rules governing the interface. This section should provide enough detailed information about the interface requirements to correctly format, transmit, and/or receive data across the interface. Include the following information in the detailed design for each interface (as appropriate):

- The data format requirements; if there is a need to reformat data before they are transmitted or after incoming data is received, tools and/or methods for the reformat process should be defined
- Specifications for hand-shaking protocols between the two systems; include the content and format of the information to be included in the hand-shake messages, the timing for exchanging these messages, and the steps to be taken when errors are identified
- Format(s) for error reports exchanged between the systems; should address the disposition of error reports; for example, retained in a file, sent to a printer, flag/alarm sent to the operator, etc.
- Graphical representation of the connectivity between systems, showing the direction of data flow
- Query and response descriptions

If a formal Interface Control Document (ICD) exists for a given interface, the information can be copied, or the ICD can be referenced in this section.

# 5 SYSTEM INTEGRITY CONTROLS

- Due to the nature of the interaction between the user and the chair itself, there is little question of integrity for the system due to it not being able to be used in a way that would cause a leak of sensitive information.
- The most likely issue would be misuse of the chair itself, such as spinning it at velocities it is not built for, however there will be a built in control and failsafe to avoid such outcomes.

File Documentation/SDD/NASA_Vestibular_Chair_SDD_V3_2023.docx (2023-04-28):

# System Design Document

For

NASA VESTIBULAR CHAIR

Team members: Brandon Boyle-Fagan Matthaeus Gebauer Miles Osborne

Dylan Prothro Noah Reid Kent Wilson

Version/Author | Date
1 | 10/6/2022
1.1 | 10/27/2022
1.2 | 11/8/2022
2.1 | 12/3/2022
2.2 | 12/4/2022
3.0 | 12/8/2022
3.1 | 12/9/2022
3.2 | 12/11/2022
4.0 | 2/18/2023
4.1 | 3/10/2023
4.2 | 4/26/2023
4.3 | 4/27/2023

# TABLE OF CONTENT

SYSTEM DESIGN DOCUMENT

## 1 INTRODUCTION

## 1.1 Purpose and Scope

The goal of the Vestibular Chair project is to restore the basic hardware functionality of a rotating chair that was acquired by Embry-Riddle that was used by NASA to test the human vestibular system and provide it with a new controller. This consists of ensuring the system can reach a specified RPM, hold that specified RPM for a set duration, and allow the servos to gradually slow down to idle. With the controller created and able to provide the intended functionality to the vestibular chair, we’ve begun integrating more modern software and hardware tools to improve the "quality of life" features of the chair. This includes a web interface, custom test profiles/sequences, and the ability to read and store sensor data from the chair.

## 1.2 Project Executive Summary

This section provides an overview of the NASA Vestibular Chair project from a macro perspective, showing the framework with which the system design was conceived.

## 1.2.1 System Overview

The NASA Vestibular Chair system can be broken down into three hardware components, the controller module, the patient remote, and the web interface. The controller module is composed of an embedded development board, motor controller module, 20x4 LCD, and other components to be able to handle digital and analog inputs for the chair motor. The patient remote is a wireless device with two buttons to indicate directionality. While the patient is spinning in the chair, the button pressed will indicate what direction they believe they are spinning. The additional web interface is planned to interface with the control module to allow for more precise measurement and input for the chair. The hardware components of the vestibular chair itself consist of a tachometer, motor, and the actual chair itself as well as some other pins setup for other once-used analog measurements. Figure 1 listed below, details a use case diagram of the NASA Vestibular chair system.

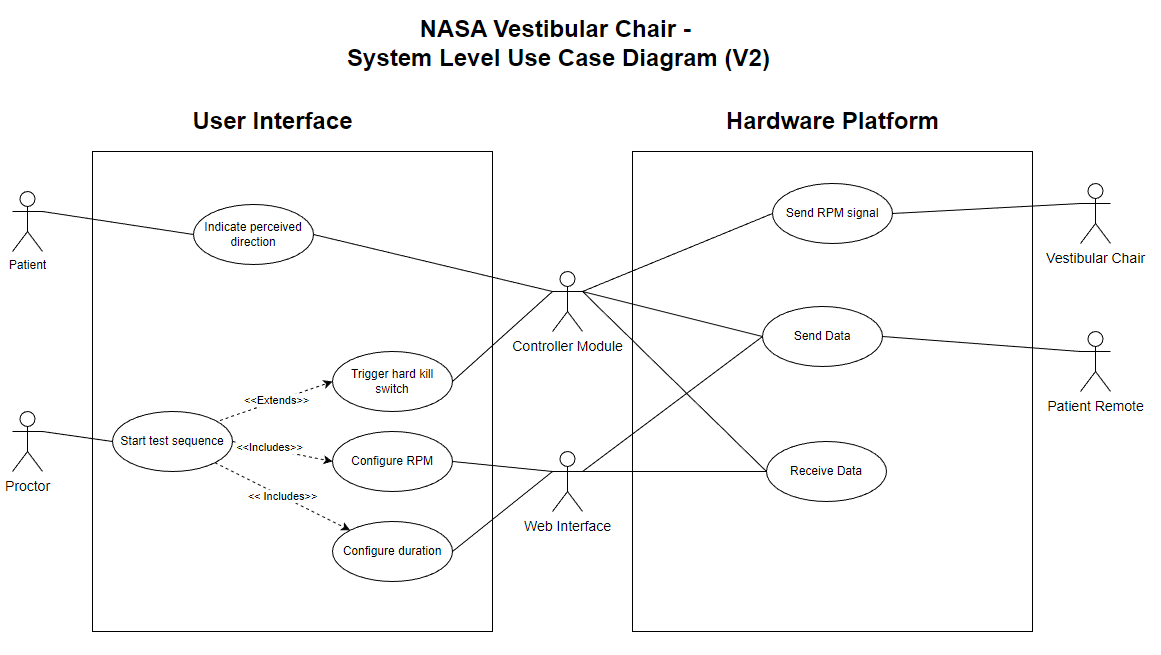
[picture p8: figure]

Figure 1: Use Case Diagram for NASA Vestibular Chair

## 1.2.2 Design Constraints

The development team plans to keep as much of the original internal hardware of the chair as possible. One of the major constraints in the design of the controller of the chair and its interface is to have the new components work with the older technology present in the chair. Another constraint comes from the speed the chair is going to be allowed to move. The chair must have a constraint to be set to not move faster than a rotation of 100 degrees per second, and with that constraint, the controller must be programmed to not allow an input of voltage that would cause a rotational speed higher than that. The controller also must have a mechanical kill switch, meaning it needs to be connected to the power being sent to the chair via the controller to be able to shut off power being sent to the chair if necessary.

## 1.2.3 Future Contingencies

Future contingencies to ensure smooth use of the controller during its lifespan include a digital part of the controller to account for any analog issues, with the intent to keep an analog and digital component to control the inputs of the chair.

## 1.2.3.1 Future Contingencies

Another contingency comes from the alternative components that the team researched in case the planned components are not available or do not work for the direction of the project. This includes researching two different types of motor controllers, Pololu - High-Power Simple Motor Controller G2 24v12 and Pololu - RoboClaw 2x15A Motor Controller (V5E). While the G2 is the preferred motor controller for the system, the functionality of the RoboClaw was investigated and was determined to be able to be used in place of the G2 if issues arise such as lack of power output or component damage.

## 1.2.3.2 Safety Measures

The inclusion of a mechanical kill switch is a contingency to avoid having the chair spin out of control if too high of a voltage is supplied to the device. Additionally, limits are placed within the software to prevent too high operation with an unstable speed.

## 1.2.3.3 Embedded Software Compatibility

Another contingency that needs to be accounted for is volatility in hardware changes, especially as it pertains to the software and drivers present in the components of the controller. Initially, this was accounted for through the STM boards due to their interchangeability code-wise, along with the code used to drive the motor controller being generic enough to not be locked into the specific motor controller that was chosen, meaning it could be used with different parts if the current one was to break for instance. However, due to better functionality on the front of data collection, the decision was made to utilize an Adafruit Feather nRF52840 express development board instead. This component is a comparable alternative to the Nucleo board we had intended to use but has the added benefits of utilizing a smaller form factor, being slightly more affordable, built-in battery charging circuitry, documented compatibility with Arduino Framework, and less complex Bluetooth libraries.

## 1.3 Document Organization

This System Design Document is organized into six sections:

    1. Introduction
    2. System Architecture
    3. Human-Machine Interface
    4. Detailed Design
    5. External Interfaces
    6. System Integrity Controls

The purpose of this document is to give the reader a comprehensive understanding of the system design and the characteristics of how the system will work.

## 1.4 Project References

No references at this time.

## 1.5 Glossary

No items to list at this time.

## 2 SYSTEM ARCHITECTURE

The system uses an interface of hardware and software to control the movement of the NASA Vestibular Chair as well as measure its speed and other readings.

## 2.1 System Hardware Architecture

The composition of the hardware is represented by:

- NASA Chair
  - The NASA chair consists of inner hardware such as its motor and sensors already installed in the device such as a tachometer, which will be used to measure the speed of the chair during operation. The sensors are used to provide feedback to the system in terms of adjusting the speed based on the present load in the chair.
- Controller Module
  - The controller module consists of a dedicated microcontroller, dedicated motor controller, and physical I/O such as a potentiometer and buttons to quickly control the state and execution of the system. The current module setup contains an Adafruit Feather nRF52840 microcontroller to control the system and interface with the Polulu G2 24v12 motor controller to achieve the desired functionality. The motor controller serves as an important factor for the operation of the motor within the chair, as it is a dedicated motor controller as opposed to having the operation handled by another component.
- Wireless bi-direction input
  - Part of the core functionality of the NASA vestibular chair is to allow the user to indicate what direction they believe to be spinning in. Due to the physical constraints of the chair spinning, we must use a wireless input to give the user this feature. The current model for this input is a controller with two buttons to indicate the direction the user believes they are spinning may that be clockwise or counterclockwise.

## 2.2 System Software Architecture

The software is centered around an embedded systems project mostly developed using C++. The development board utilized is the Adafruit Feather nRF52840 Express which has extensive compatibility with the Arduino Framework. More importantly, the manufacturer, Adafruit, has developed a Bluetooth library for use with the onboard Bluetooth module. Due to the urgency of the project, writing drivers for each component of the project is not feasible and would artificially and unnecessarily increase the difficulty of the project.

The Adafruit Feather nRF52840 Express is the core of the controller module and will interface with several peripherals including the motor controller and a 20x4 LCD. Both peripherals can be controlled via the I2C protocol which makes the software written easier to implement and maintain.

The second aspect of the system is the web interface which gives the proctor more options as it relates to creating test sequences and displaying data during the test. Data is read from the chair via the analog pins and then temporarily stored in a buffer. The data is then sent over UART to the web interface and displayed on the host computer. Likewise, when the proctor wants to actuate the chair, they will use the web interface to configure the test.

When ready, the test sequence information will be sent via commands over UART and then processed by the Adafruit development board. The system shall then begin to follow the sequence of events as indicated by the proctor’s designated test sequence.

A state transition chart for the system excluding the web interface is listed below in Appendix A and Appendix B. The web interface was excluded at this time to focus on the current priority of more robust mechanical control. However, when the web interface and accompanying features are introduced, the state transition chart should be very similar.

## 2.3 Internal Communications Architecture

In the NASA Vestibular Chair System, the main communication channels happen over UART from sending and receiving commands from the web interface and processing digital signals from the controller module I/O. Additionally, I2C will be utilized by the Adafruit development board to interface with the motor controller and the seven-segment displays. Lastly, Bluetooth will be utilized to receive data from the wireless input device indicating what direction the user believes they are spinning in. This is feasible because the Adafruit Feather nRF52840 Express has a built-in Bluetooth module. Figure 3 below describes the internal communication between the system components. This figure does not consider the protocol or medium used for communication.

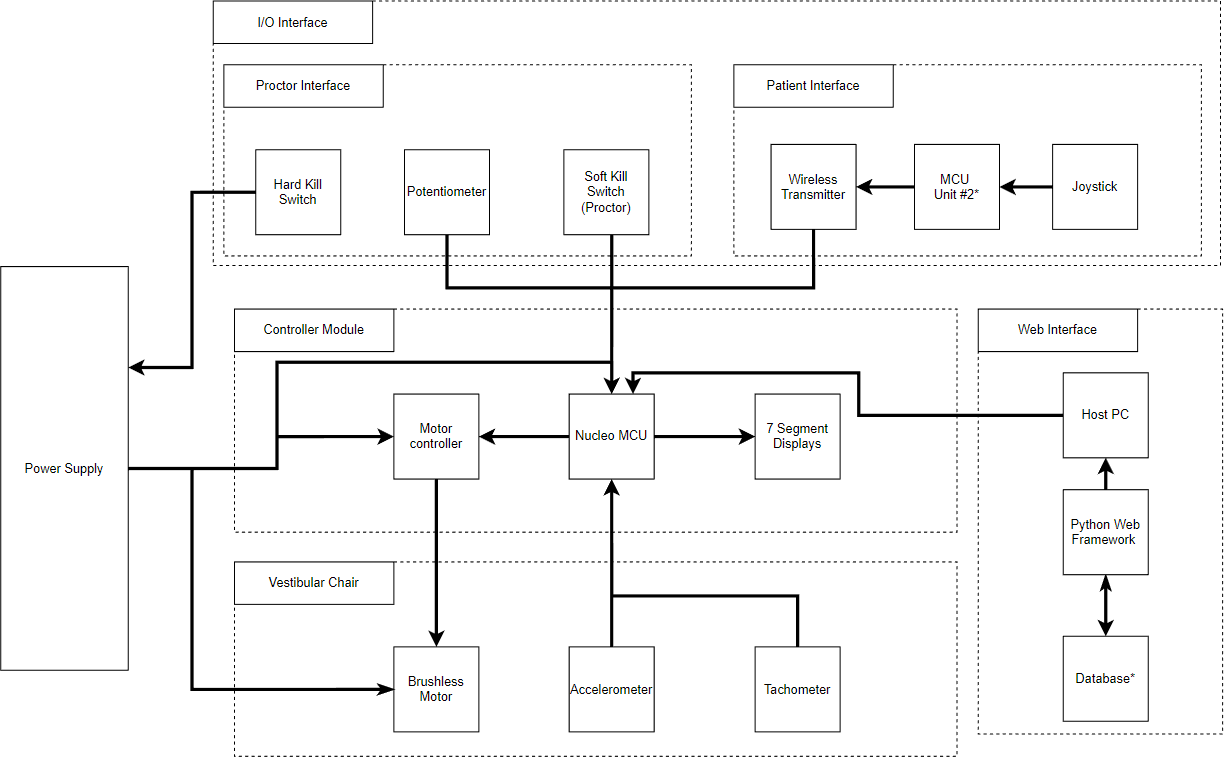
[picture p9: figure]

Figure 3: High-Level Hardware Communication Overview

Regarding communication between core systems, Bluetooth LE and UART are utilized. To collect data from the patient remote, a peer-to-peer connection between the controller module and the patient remote is established. While Bluetooth is bi-directional, the method utilized here is uni-directional such that the control module operates as the receiver and the patient remote will serve as the transmitter. When the chair is in operation and a connection is established, the remote will send packets of data the control module will log and process.

The latter two items are physical connections. The web interface is intended to use UART/serial to interface with the control module. Note that the web interface will be hosted on a desktop/laptop system with USB ports. Even though the physical UART pins are not utilized, the USB ports being used are capable of converting a USB signal to a UART-compliant packet. Sending commands to the vestibular chair is done through an analog signal generated by the motor controller component and carried through a Cat 6 ethernet cable. Figure 3.1 listed below details the communication architecture between the critical components of the system.

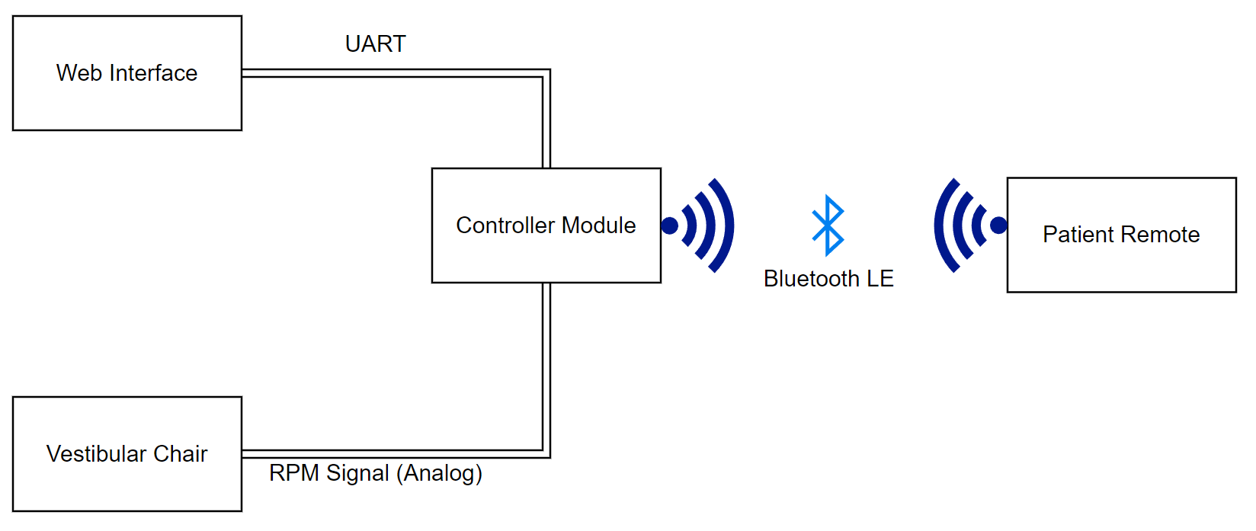
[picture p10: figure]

Figure 3.1: System-Level Communication Overview

Figure 4 listed below is a simple data flow diagram, detailing the critical piece of information being transferred from components. To make the diagram simpler, the controller module is assumed to include all required electronics including the Adafruit development board, G2 motor controller, seven-segment displays, switches, and potentiometers.

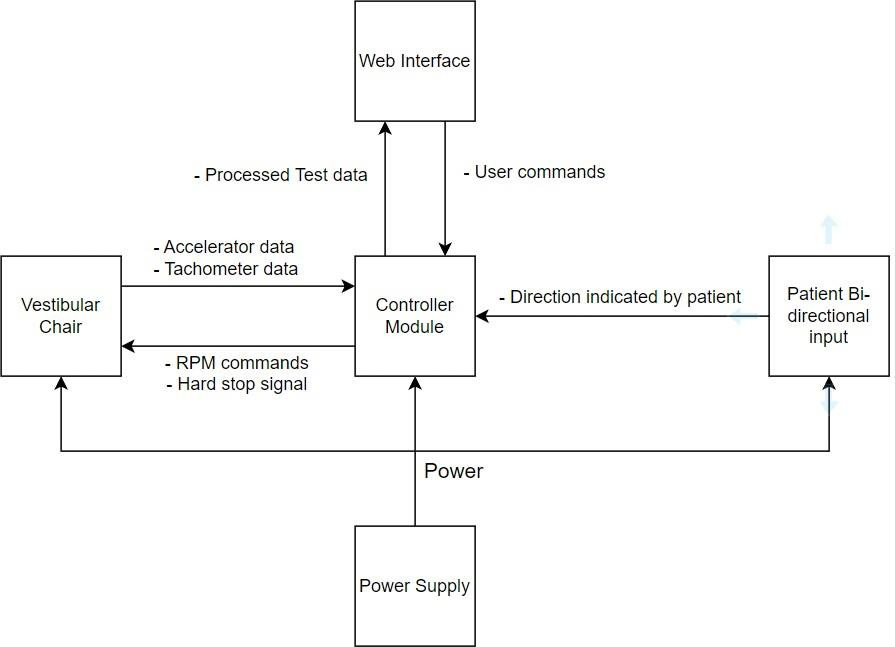
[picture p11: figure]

Figure 4: Level 0 Data Flow Diagram for NASA Vestibular Chair System

## 3 HUMAN-MACHINE INTERFACE

Human input is required to determine the speed of the vestibular chair and by association, the voltage and amperage required to achieve that speed. This interaction will cause the user to be able to adjust the chair’s speed through the controller device.

## 3.1 Inputs

The inputs of the system will be given from the controller to the chair to allow movement of the chair or to set up testing cases for the speed to be applied without needing to be adjusted by the user physically. These inputs are user-generated, as the individual in control of the device sets the RPM that the chair is being given through test cases. The sensors used will also count as input, including things such as the tachometer and accelerometer. Another input will come from the individual sitting in the chair, as they will be able to send data indicating the direction, they believe they are spinning in with the bi-directional input device.

## 3.2 Outputs

The output response from the chair should be the tachometer reading to feed into the controller to control the speed via its feedback. This will allow the system to avoid reaching a speed that outpaces the scope of the controller. The other output is that given from the chair itself, which is its actual rotation given the input voltage supplied by the controller. The feedback from the chair should also be able to communicate the direction it is rotating to the controller. The bi-directional controller will also have an output of which direction the user indicated they were spinning in.

## 4 DETAILED DESIGN

This section contains detailed information about the hardware and software design of the system.

## 4.1 Hardware Detailed Design

The system is centered around the Adafruit Feather nRF52840 Express. This component will perform the following roles at a minimum:

1. Accept user input from the proctor
2. Perform data acquisition at a sampling rate of at least 20hz
3. Process commands sent via UART
4. Send data to peripherals through I2C
5. Process commands via Bluetooth from wireless bi-directional input
6. Send data to the web interface via UART
7. Control the vestibular chair’s RPM via commands sent to the motor controller.

Figures 5, 6, and 7 are a simplified overview of the hardware and components present in the system. Note, that these diagrams do not document the internal communication between each module.

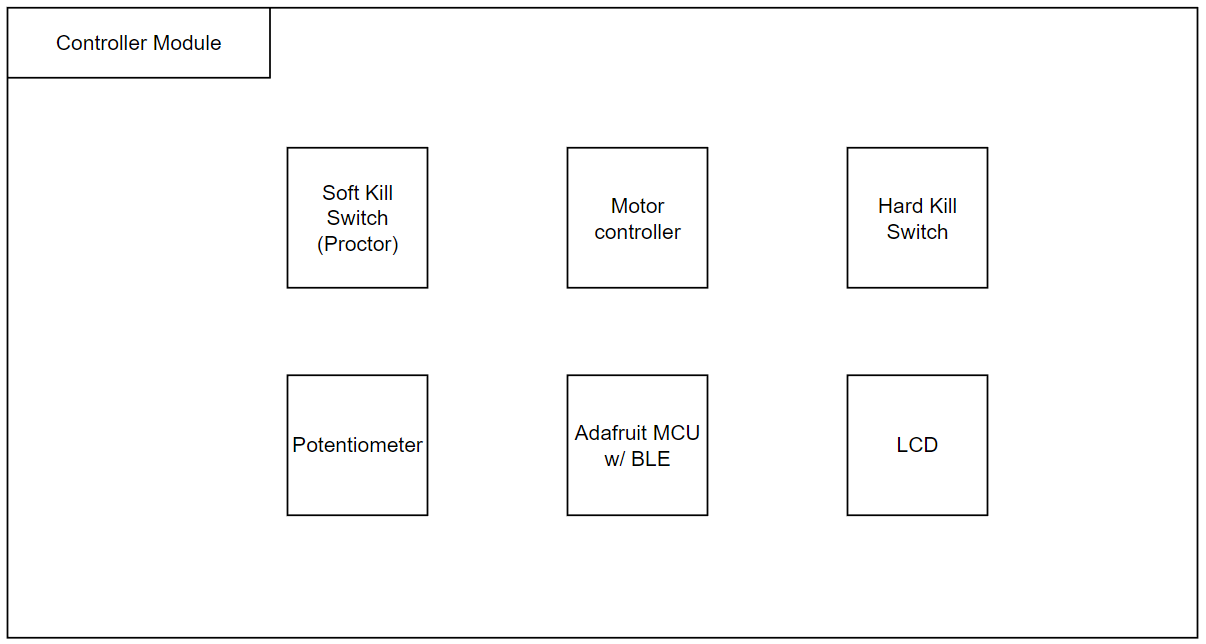
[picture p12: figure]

Figure 5: Simplified overview of NASA Vestibular Chair Controller Module

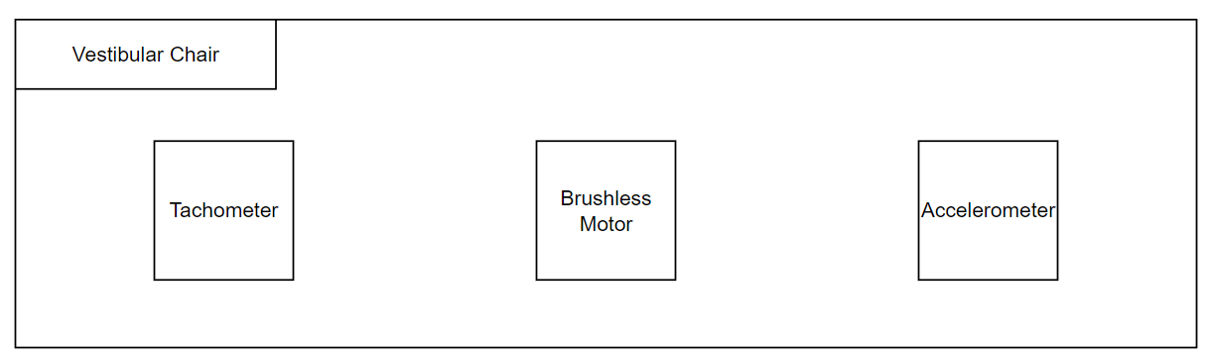
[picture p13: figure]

Figure 6: Overview of NASA Vestibular Chair Components

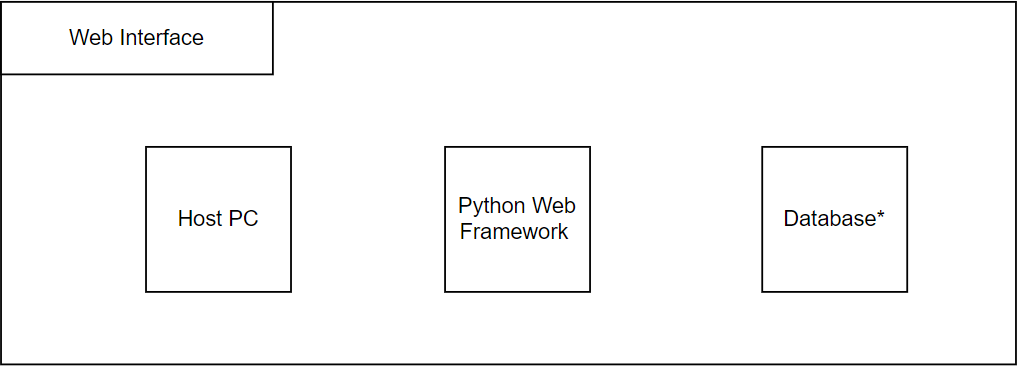
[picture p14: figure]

Figure 7: Overview of Web Interface Components

## 4.2 Software Detailed Design

This system is compromised of multiple components and interfaces which exceed the scope of the document to discuss at length. However, the system can be condensed and discussed based on the five major components and the software dependencies of each. Those components consist of the following:

    1. Vestibular chair
    2. Controller Module
    3. Patient remote
    4. External logging application
    5. Mbientlab Bluetooth IMU*

A simple architecture diagram is presented below in Figure 8. It is worth noting that item five from the list above was a recent addition to the system and existing figures have not been updated to account for the inclusion.

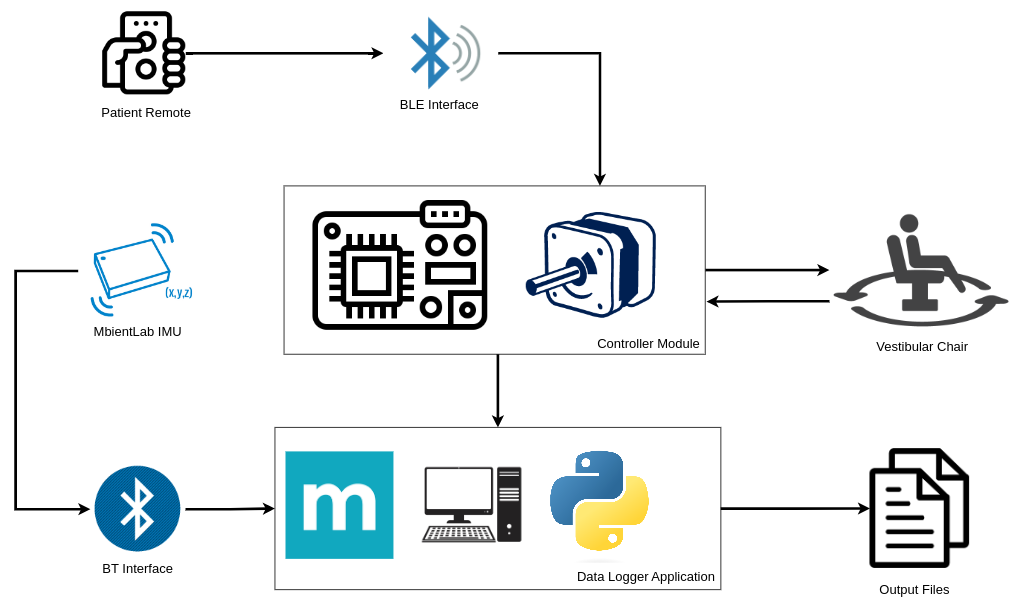
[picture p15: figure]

Figure 8: Simplified system architecture diagram

## 4.2.1 Vestibular Chair

The vestibular chair itself has no software dependency or built-in software system. Its operation is solely dependent on the inputs of the controller module. Safety mechanisms are built in to prevent unintended or non-deterministic behavior. For outputs, the value of the onboard tachometer is obtained by the controller module and logged by the data logging application.

## 4.2.2 Controller Module

The controller module contains the main processing capabilities of the system. Since we utilized the Adafruit Feather nrf52840 express microcontroller, the language utilized was C++ with the Arduino framework. Writing drivers for the hardware in C/C++ or using Python was available but utilizing the Arduino framework removed the need to develop and test our drivers when there is sufficient support and documentation with the Adafruit Feather board and the Arduino framework. Likewise, our development environment was Visual Studio Code (vscode) with the Platformio extension. The Platformio extension allowed us to utilize a more capable development tool with library management, version control, and multiple build configurations.

The Adafruit Feather microcontroller had to interface with a Pololu motor controller, an LCD, and another Adafruit microcontroller contained in the patient remote through Bluetooth. The interface between the motor controller and LCD was accomplished through the I2C protocol. The Arduino wire library provided the API for completing the I2C transactions for both peripherals mentioned. In particular, the exact communication scheme for the motor controller is mentioned in a later section.

Bluetooth communication was achieved through the use of the provided Adafruit Bluefruit Bluetooth libraries. There are specific configurations for the nrf52 Bluetooth modules utilized on the Adafruit microcontrollers which were utilized. After understanding how to utilize the libraries, we configured the module to only connect and respond to messages sent by the patient despite the potential presence of other Bluetooth signals in the area.

The last aspect of the controller module is the communication between itself and the data logging application. From the perspective of the controller module, communication is accomplished through the use of the Arduino Serial library and Software serial libraries. These libraries utilize the UART protocol which sends messages to the data logging application through USB.

## 4.2.3 Patient Remote

The patient remote is much simpler than the controller module. Its only functionalities are to respond to button presses by the patient in the chair, connect to the controller module via Bluetooth, and send the button press data to the controller module. Its development environment is identical to the controller module due to the use of identical microcontrollers. To make the process easier, we have configured both modules to only connect to each other despite the potential presence of other Bluetooth signals in the area.

## 4.2.4 Data Logging Application

The data logging application was developed in Python and runs on an external laptop during the trials. Currently, the application only runs on Windows 10 but Windows 11 support should be functional. Development of the tool is only supported on Windows machines at this time. Linux development was previously possible but the inclusion of packages to connect with the MbientLab MMS IMU has suspended that development. The development environment utilized consists of Python 3.9 and the PyCharm ide for easy integration and package management. To keep the application simple as possible, only a few external dependencies were included with the project. Pyserial was utilized to initialize and conduct serial communications between the controller module. Additionally, the Mbientlab Metawear package was utilized to conduct with the Bluetooth IMU. This package was not difficult to integrate but does require that the host PC running the application has a Bluetooth module on board that was enabled and that the respective IMU was in extreme proximity to be connected.

## 4.2.5 Bluetooth IMU

The Mbientlab MMS IMU was a recent addition to the system. Adding this component came about due to the discovery that the tachometer in the vestibular chair was likely damaged at some point. The data recorded was extremely noisy and irregular to an extent that made it unusable. After discussion, the decision was made to incorporate an off-the-shelf wireless component that would seamlessly integrate with our existing system. While the IMU comes equipped with a fully-fledged sensor suite including sensor fusion, we are only concerned with the gyroscope values produced by the BMI270 sensor inside. As mentioned above, the IMU connects with the data logging application through the open-source Mbientlab Metawear package. Gyroscope values are then streamed and processed by the external application which is utilized to determine when the chair comes to a complete stop.

## 5 EXTERNAL INTERFACES

The current external interface is the plan to add a web-based component for the controller. With the controller module design showing positive results, focus on the web interface has been prevalent although it has yet to be completely flushed out. However, it will interface with the controller and serve as the main function for the proctor to interface with the chair and its testing capabilities.

## 5.1 Interface Architecture

The web interface will interface and interact with the microcontroller of the system which is serving as the main driving force for the motor controller, which powers the chair. This level of interaction will allow the user of the web interface to dictate a certain test sequence via specific parameters such as the length of the test and the speed of rotation for the chair. This will then run through the microcontroller board which will run the code to follow those parameters when it sends data to the motor controller, effectively controlling the rotation of the vestibular chair.

## 5.2 Interface Architecture

This section details specifications regarding the communication methods for the essential modules of the NASA Vestibular chair system. The figure below gives an overview of how data is transferred between components and the protocol or method utilized. This figure also indicates the directionality of the data sent.

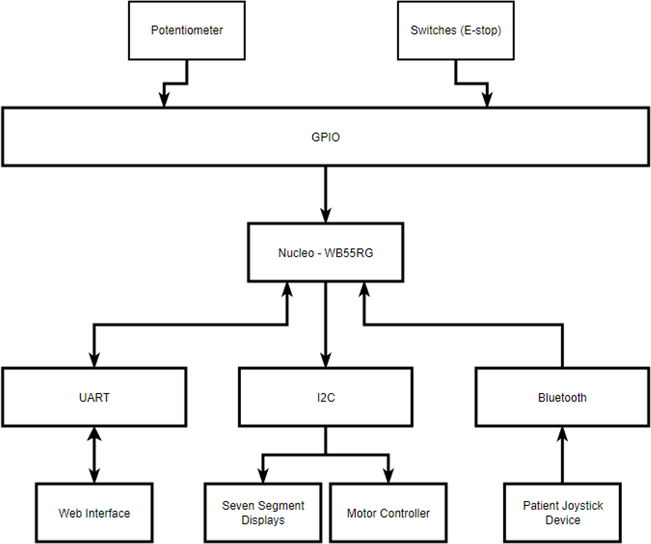
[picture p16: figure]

Figure 9: Internal Communication Architecture of NASA Vestibular Chair

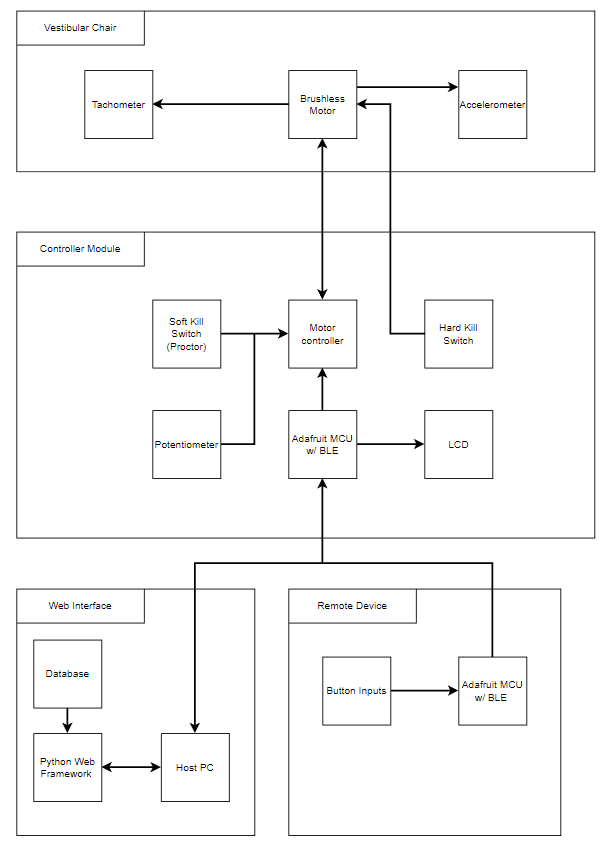
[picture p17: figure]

Figure 9.1: Detail view of Internal Communication Architecture

## 5.2.1 Motor Controller Interface

The Pololu Simple Motor controller interfaces with the control module via the I2C protocol. Details of the I2C specification can be found here. (http://www.cs.columbia.edu/~cs4823/handouts/UM10204.pdf) Pololu provides a reference manual (https://www.pololu.com/docs/0J77) on how to properly initialize and use the motor controller. For our system, the motor controller will be set to the Binary mode to process all commands over I2C. All commands sent to the motor controller shall follow the compact protocol which places the command in the first byte sent and the following commands indicate parameters for the commands. The graphic below indicates the packet format of the command in a binary representation.

Figure 10, I2C, Compact Protocol Packet

A list of valid commands is also included in Pololu’s documentation. The commands include but are not limited to: “motor reverse”, “motor forward”, “set motor limit”, and “set current limit”. Commands are distinguished by sending bytes with a decimal value between 128 and 255 while data bytes are any value between 0 and 127.

## 5.2.2 Web Interface

The web interface component of the system will utilize the UART protocol for transmitting data between the host PC and the control module. A formal standard or Interface Control Document (ICD) has not been defined at this time due to the current objective of establishing simple hardware control. However, after reaching this milestone, it shall be included in the next version in a later version.

## 5.2.3 Patient Input Device

The patient input device will be utilizing the same development board that the control module is based on. Subsequently, the patient remote device is Bluetooth-capable and supports the BLE specification. Furthermore, the Adafruit Feather nRF52480 Express has support for this protocol and sufficient documentation to utilize it. A formal standard or Interface Control Document (ICD) to define the transfer of data has not been defined at this time due to the current objective of establishing simple hardware control. At the time of writing, that objective has just been achieved. For the final release of this document, a formal interface standard will be included.

## 6 SYSTEM INTEGRITY CONTROLS

Due to the nature of the interaction between the user and the chair itself, there is little question of integrity for the system due to it not being able to be used in a way that would cause a leak of sensitive information. The most likely issue would be a misuse of the chair itself, such as spinning it at velocities it is not built for. However, there are built-in controls and fail-safes to avoid such outcomes.

## 7 Appendix A

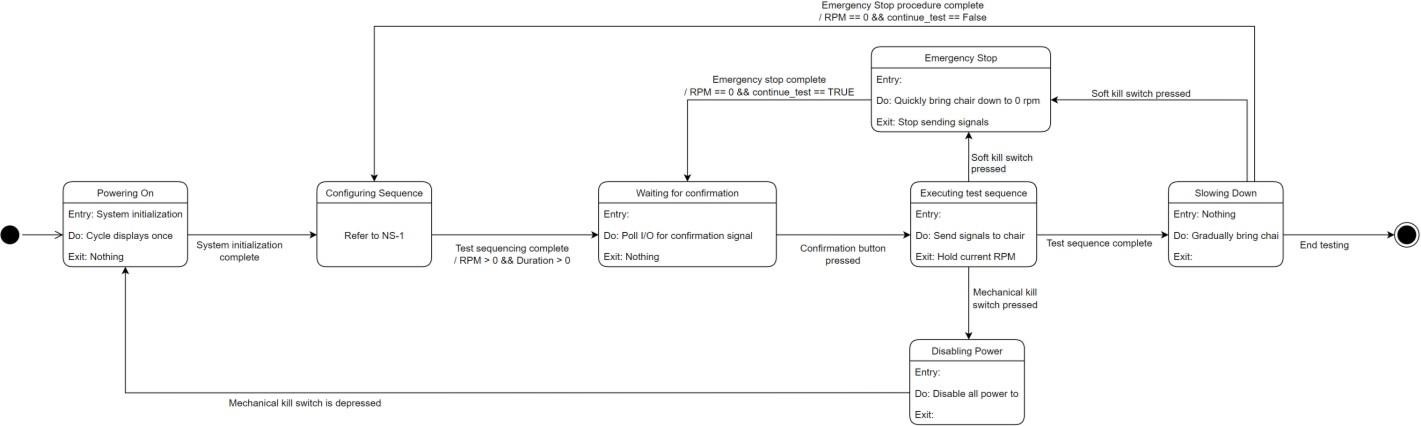
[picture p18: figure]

Figure 2: State Transition Chart for NASA Vestibular Chair

## 8 Appendix B

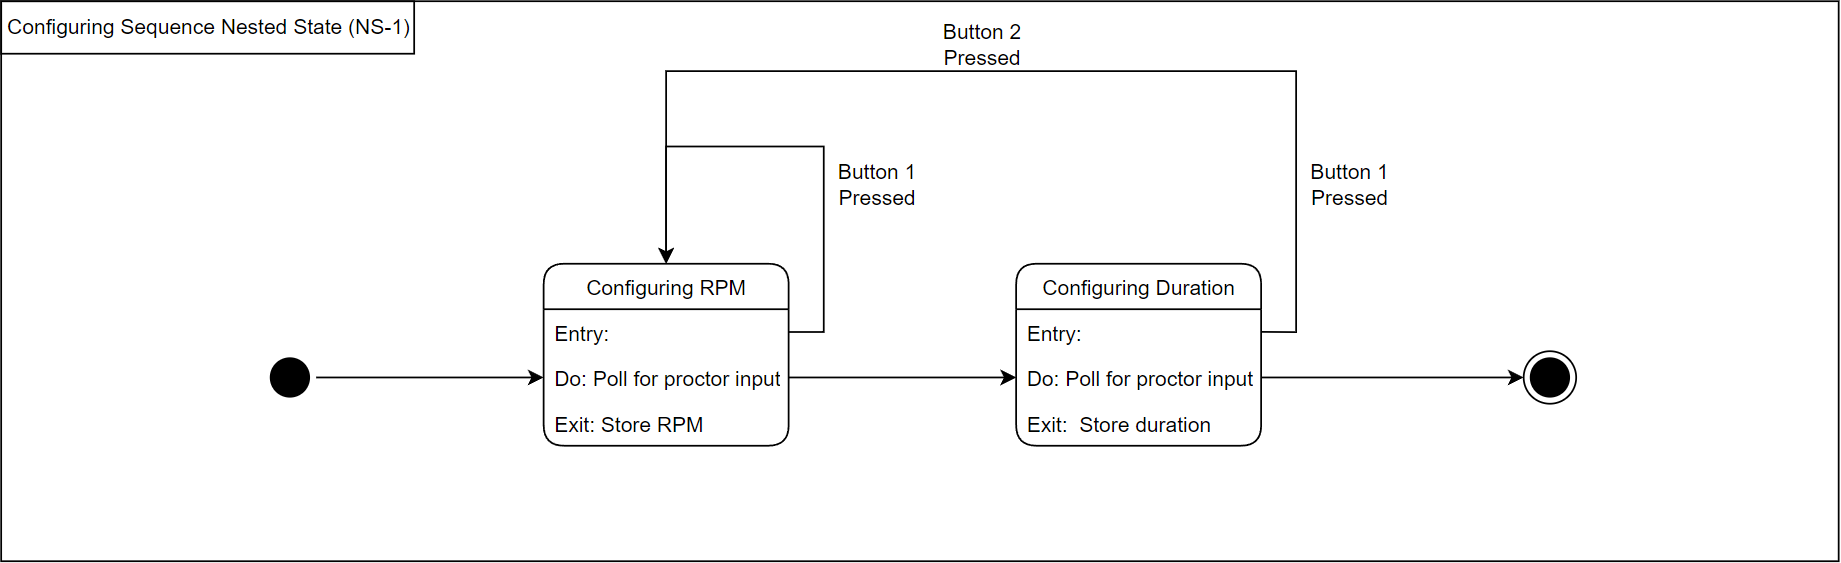
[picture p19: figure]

Figure 2.1: Nested State 1 for State Transition Chart (NS-1)

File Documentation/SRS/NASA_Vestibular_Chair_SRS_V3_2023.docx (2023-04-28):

# System Requirements Specification for

# NASA Vestibular Chair

Dylan Prothro Brandon Boyle-Fagan

Miles Osborne Noah Reid Kent Wilson

Matheus Gebauer

Embry-Riddle Aeronautical University

Start Date: 10/7/22 Last Updated: 4/27/23

# Revision History

Name | Date | Reason For Changes | Version
Initial Draft (V1 Draft) | 10/7/202 2 | Initial Release | 0.1
V2 WIP | 10/30/22 | Update system requirements | 0.11
V2 | 11/8/22 | Version 2 release | 0.2
V3 WIP | 12/7/22 | Response to V2 comments | 0.21
V3 Format Updates | 12/9/22 | Added more requirements, changed formatting | 0.3
V4 WIP | 2/20/23 | Adjustment of system requirements (removal, addition) | 0.4
V4 | 4/26/23 | Finalization of V4 release, updated user-manual link | 0.4

# Table of Contents

# Introduction

This project is designed with the purpose of restoring functionality to the NASA Vestibular Chair. The device was originally used in the late 1960s to conduct experiments and trials for astronauts and pilots to assess vestibular ocular reflex suppression. The purpose of the restoration is to conduct trials to study vestibular system illusions.

The chair was actively involved in research at NASA and was recently acquired by Embry-Riddle Aeronautical University faculty. This project involves restoring its basic functionality and then adding software functionality to improve the ease of use.

## 1.1 Purpose

The purpose of this document is to describe the requirements and constraints for restoring and operating the refurbished NASA vestibular chair. This document consists of specifications regarding the chair itself, the interaction between software and hardware, interactions between intended users, and any safety or legal standards that must be adhered to.

## 1.2 Document Conventions

Nothing to list at this time.

## 1.3 Intended Audience and Reading Suggestions

The intended users of this product include aerospace physiology researchers, pilots, astronauts, astronaut candidates, and engineers. This document contains information regarding the requirements and general functionality of the restoration of the NASA vestibular chair.

## 1.4 Product Scope

When the chair was given to researchers at Embry-Riddle Aeronautical University, its functionality was unknown. The last time the chair was operated would have been at least 30 years ago. Furthermore, the original controller used has been lost and its whereabouts are unknown. However, thanks to external support, documentation from the manufacturers of the chair has been acquired which provided the starting point for this project. The goal of this project has been to analyze the current state of the chair, determine its state of functionality, resolve any mechanical abnormalities, and expand on its basic functionality.

The original purpose of this chair was to study vestibular illusions that occur from flight. Once the project has been completed, the chair will be used to conduct research trials into spatial disorientation.

## 1.5 References

No references at this time.

# 2. Overall Description

Section 2 discusses the overall purpose of the product. Each section details a specific aspect of the project as follows:

  - Section 2.1 – Product perspective
  - Section 2.2 – Product functions
  - Section 2.3 – User classes and characteristics
  - Section 2.4 – Operating environment
  - Section 2.5 – Design and implementation constraints
  - Section 2.6 – User documentation
  - Section 2.7 – Assumptions and dependencies

## 2.1 Product Perspective

The original implementation of the vestibular chair relied on an external control interface/station where a user could send commands to the chair. The restored design will follow the same design with a host station displaying a web interface to allow for commands to be sent to a dedicated hardware controller. The commands are then processed by the dedicated hardware controller and the vestibular chair will execute the desired command.

The SRS will focus on the controller module and the web interface. The operations of these items are essential to the operation of the restored NASA vestibular chair.

### 2.1.1 Controller Module

The controller module is the dedicated hardware controller that processes commands, performs data acquisition, and communicates with the web interface. The controller module consists of an Adafruit Feather nRF52840 Express microcontroller, Pololu Simple Motor Controller G2, an LCD screen, and physical I/O devices including but not limited to buttons, and potentiometers. A dedicated hardware controller was implemented to establish a baseline for controlling the chair, prevent the scope of the web interface from exceeding the intended purpose, and to take advantage of the physical I/O devices. Without the dedicated hardware, the proctor would have to solely rely on the web interface and have no means to physically control the chair.

### 2.1.2 Web Interface

The web interface is intended for the proctor’s use only. This item gives the proctor more functionality as it pertains to controlling the chair and running tests. With the web interface developed, the goal is to give the proctor the means to configure a test sequence, as well as start the test, and export the test data to a csv file, all without the need to use the physical I/O components.

### 2.1.3 Bi-Directional User Input Device

As requested for testing purposes, the user shall be given the ability to indicate the direction they think they are spinning throughout the test. The most efficient way this was deemed to be possible was a wireless bi-directional input. While the design becomes refined and adjusted, the core objectives are as follows: (1) give the user the ability to indicate what direction they think they are spinning (clockwise, counterclockwise, stationary), (2) send the aforementioned data to the controller module to be processed, (3) give the user the ability to stop the test in case of an emergency.

## 2.2 Product Functions

- Actuate the analog motors to spin the user at a specified rate
- Collect data from the on-board sensors and external peripherals
- Collect data from the user through the use of wireless peripherals
- Log all collected data in a human-readable format
- Manage and start test sequences from the web interface
- Stop the test in the event of an emergency

## 2.3 User Classes and Characteristics

### 2.3.1 Patient

The patient is the user who will sit in the chair and take part in the experiment(s).

Their role is to indicate what direction they believe they are spinning in throughout the test. This is accomplished via a bi-directional input device in the form of a pair of buttons to indicate the direction. Furthermore, the user may also indicate when they are not spinning by not orienting the control interface in either direction.

### 2.3.2 Proctor

The proctor will be responsible for interacting with the web-based user interface.

Additionally, they will be responsible for configuring, selecting, and executing the test sequence. As a safety precaution, the proctor will have the ability to press/depress the mechanical kill switch in the event of an emergency where the currently running test or sequence needs to be canceled immediately.

## 2.4 Design and Implementation Constraints

### 2.4.1 Design Constraints

      - The system cannot operate at greater than 12v. Beyond this range introduces bodily harm to the patient.
      - No one can be within the chair’s range of motion or diameter during operation except the patient sitting in the chair.

### 2.4.2 Implementation Constraints

      - Accelerometer data will be limited by the capability and resolution of the on-board accelerometer.
      - Tachometer data will be limited by the capability and resolution of the onboard tachometer.
      - Due to the chair spinning, a wired bi-directional input for the user is not feasible.
      - Desired RPM is also dependent on the patient’s weight and posture in the chair.

## 2.5 User Documentation

Vestibular Chair User Manual: https://github.com/prowl107/NASA-Vestibular-Chair/blob/main/Documentation/User%20Manual/NASA_Chair_User_Manual.pdf

## 2.6 Assumptions and Dependencies

Nothing to list at this time.

# 3. System Features

Section 3 covers information regarding the usage and core functionality of the system. Sections 3.1 outlines the motor control requirements. Section 3.2 details the data acquisition for the system. Section 4.3 outlines user input and feedback. Sections 4.4 and 4.5 outline the web interface and controller requirements respectively.

## 3.1 Chair/Motor Control

### 3.1.1 Description and Priority

The system must provide a reliable means to control the brushless motor built into the vestibular chair. This includes aspects such as bringing the chair to the desired speed and then gradually lowering the speed to 0 RPM when the test has completed, or an emergency has been detected.

### 3.1.2 Stimulus/Response Sequences

When the proctor arms the system and indicates that the test is ready to start, the chair should be rotating. At the end of the test sequence, the test should return to 0 RPM.

### 3.1.3 Functional Requirements

REQ ID | Requirement
SYS-1 | The system shall allow the chair to spin up to a specified RPM determined by the proctor
SYS-2 | After a specified duration set by the proctor, the chair shall enter a free coast state
SYS-3 | The system shall adjust the voltage to the motors in response to the user's weight

| to maintain the desired rate/RPM
SYS-4 | The system shall not exceed 100 degrees per second (1 revolution every 3 seconds) at any point during its operation
SYS-5 | While the chair has not reached the target RPM during operation, the system shall gradually increase the speed by 1.15° degrees per second
SYS-6 | If the chair reaches the target RPM, the system shall stop increasing the speed of the chair.
SYS-7 | The chair shall not spin faster than the target RPM under any circumstance
SYS-70 | The control module shall maintain wireless communication with the patient remote throughout the entirety of each trial

NOTE: Target RPM is set by the proctor during the setup phase of operation.

## 3.2 Data Acquisition

### 3.2.1 Description and Priority

Acquiring data for analysis is an objective of this project as well. The system must record multiple pieces of data and display the information to the proctor. Furthermore, the data must be sampled at a fast enough rate to generate an accurate set of data with little error. This data should be viewable via the web interface or through any application that supports viewing of csv files.

### 3.2.2 Stimulus/Response Sequences

Data acquisition should begin as soon as the test sequence begins. Data will be viewable during the test and after the test concludes.

### 3.2.3 Functional Requirements

REQ ID | Requirement
SYS-8 | The system shall record the chair's current position (steady state)
SYS-9 | The system shall record the desired rpm set by the proctor
SYS-10 | The system shall record the rpm that the chair is currently spinning at
SYS-11 | The system shall record the time elapsed during the current test sequence
SYS-12 | When the user indicates via the bi-directional control method, the system shall record the total time the user indicates they are spinning
SYS-13 | When the user indicates via the bi-directional control method, the system shall record the direction they think they are spinning in
SYS-14 | When the user indicates via the bi-directional control method, the system shall record timestamps of when the button is triggered
SYS-15 | The system shall have the ability to export data in a human-readable format
SYS-16 | The system shall record acceleration data
SYS-17 | The system shall record tachometer data
SYS-18 | The system shall record all commands sent to the controller
SYS-19 | The system shall record data at a sample rate of at least 20 HZ
SYS-68 | The system shall record the time when the hair comes to a complete stop after the trial duration has elapsed
SYS-69 | The system shall continue to record data until the proctor has signaled the end of the test

## 3.3 User Input/Feedback

### 3.3.1 Description and Priority

The patient and proctor are both expected to interact with the system. In particular, the patient’s input for what direction they are spinning in is a key deliverable of the system. The proctor is responsible for configuring, starting, and stopping the tests.

### 3.3.2 Stimulus/Response Sequences

The proctor’s input will begin as soon as the system has powered on and will last as long as the system is active. The user can begin interacting with the system as soon as the test sequence has begun.

### 3.3.3 Functional Requirements

REQ ID | Requirement
SYS-20 | The system shall support user input from a wireless bi-directional human input device
SYS-21 | The system shall allow the user to indicate what direction they are spinning via a bi-directional control method
SYS-22 | The system shall record intermediate values for the direction indicated
SYS-23 | The system shall interface with a wireless bi-directional human input device such as a joystick or button
SYS-24 | The proctor shall be able to press the "soft" kill switch (software) during operation to stop the chair in the event of an emergency
SYS-25 | The proctor shall only be able to actuate the chair or start a test after a unique button/switch is pressed (arming switch)
SYS-26 | The proctor shall be able to terminate power delivery to the chair by pressing a mechanical switch
SYS-27 | The proctor shall set the duration of the test either via web interface or the controller module

## 3.4 Web Interface

### 3.4.1 Description and Priority

The web interface is a requested feature to make it easier for the proctor to interact with the chair and collect data. While the web interface can be used to configure the test sequence, it does have greater priority than the control module.

### 3.4.2 Stimulus/Response Sequences

The web interface shall allow proctor input as soon as a valid connection between the control module and the host PC has been established.

### 3.4.3 Functional Requirements

REQ ID | Requirement
SYS-28 | The system shall support communication between an embedded target and a web interface via the UART protocol
SYS-29 | The web interface shall support the exporting of data in a csv (or equivalent) file format
SYS-30 | The web interface shall allow the operator to add different test sequences
SYS-31 | The web interface shall display the system’s status while the web interface is active, and a connection is established
SYS-32 | The web interface shall not execute any commands unless the proctor has armed the system
SYS-33 | The web interface shall not execute any commands unless connection with the control module has been established
SYS-34 | The web interface shall not allow for user input unless connection with the control module has been established

## 3.5 Control Module Processing
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

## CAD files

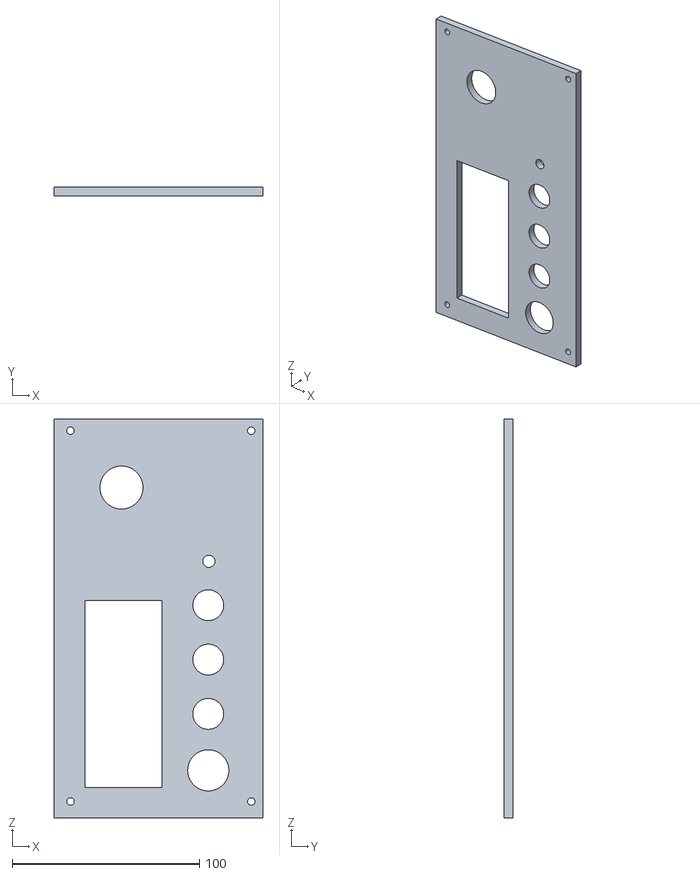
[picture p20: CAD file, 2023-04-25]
Engineering Notebook/Brandon Boyle-Fagan/SD boxes/component box cover.stl
111.8 x 4.83 x 213.4

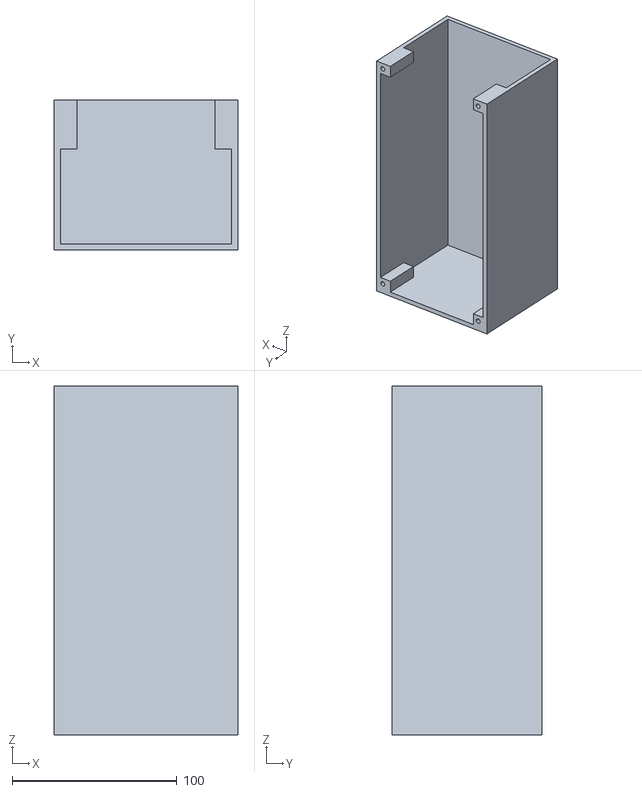
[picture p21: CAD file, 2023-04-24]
Engineering Notebook/Brandon Boyle-Fagan/SD boxes/Component box Bottom.stl
111.8 x 91.4 x 212.1

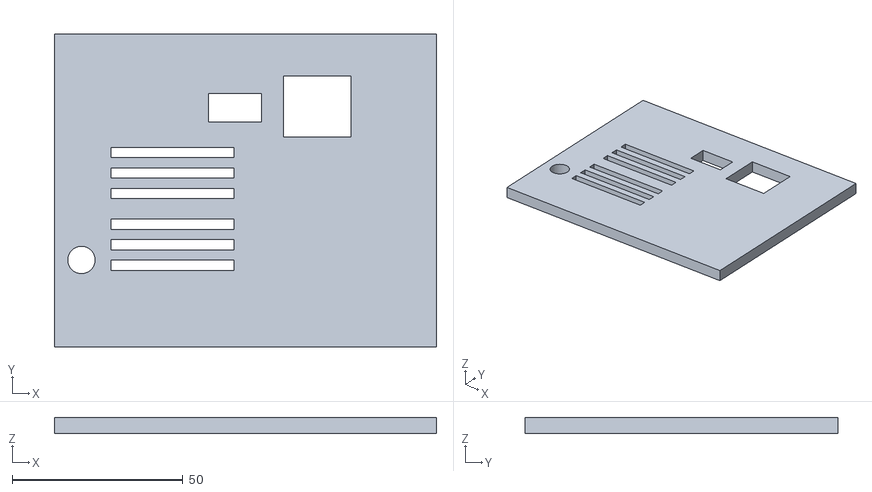
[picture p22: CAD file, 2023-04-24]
Engineering Notebook/Brandon Boyle-Fagan/SD boxes/compnent box front.stl
111.8 x 91.4 x 4.83

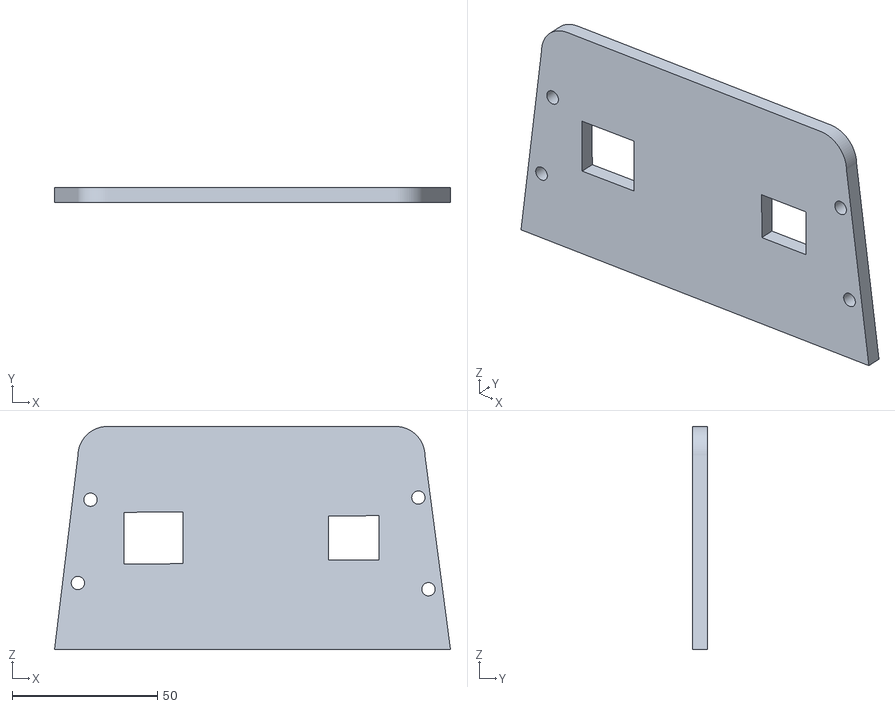
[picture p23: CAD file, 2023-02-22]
Engineering Notebook/Brandon Boyle-Fagan/SD boxes/chair power plate.stl
136.1 x 5.08 x 76.7

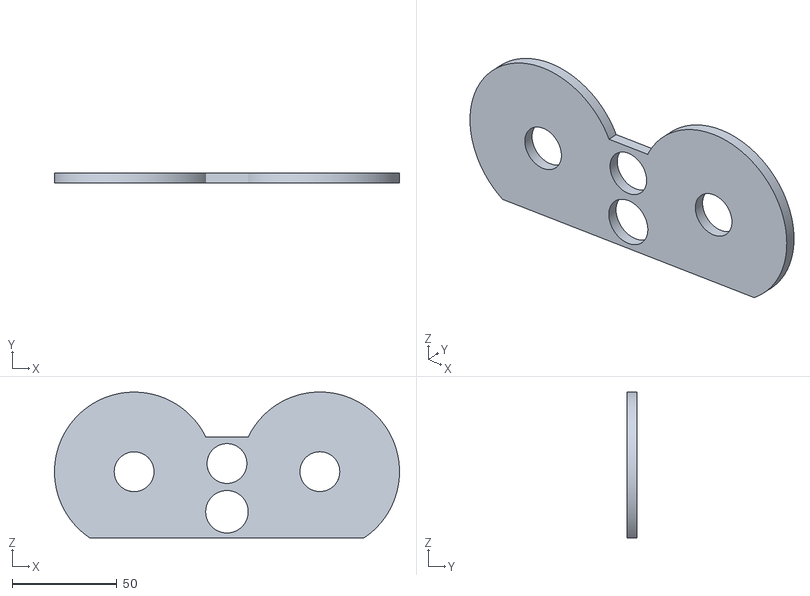
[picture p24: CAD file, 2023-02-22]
Engineering Notebook/Brandon Boyle-Fagan/SD boxes/paitent remote top.stl
165.1 x 4.83 x 69.8

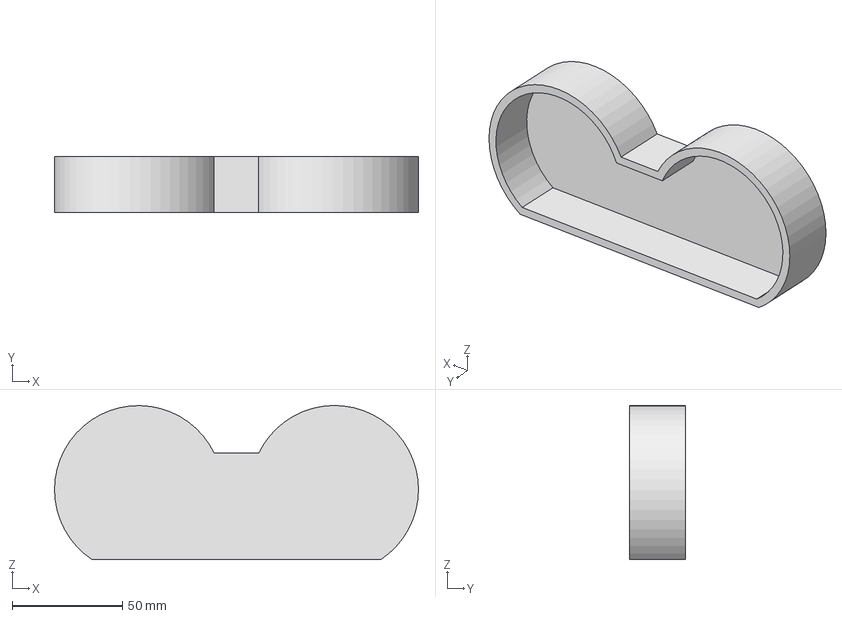
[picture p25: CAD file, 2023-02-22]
Engineering Notebook/Brandon Boyle-Fagan/SD boxes/paitent remote box.stp
165.1 x 25.4 x 69.8 mm

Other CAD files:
Engineering Notebook/Brandon Boyle-Fagan/SD boxes/Component box Bottom.ipt
Engineering Notebook/Brandon Boyle-Fagan/SD boxes/OldVersions/Component box Bottom tall L.0001.ipt
Engineering Notebook/Brandon Boyle-Fagan/SD boxes/OldVersions/Component box Bottom tall R.0002.ipt
Engineering Notebook/Brandon Boyle-Fagan/SD boxes/OldVersions/Component box Bottom tall.0003.ipt
Engineering Notebook/Brandon Boyle-Fagan/SD boxes/OldVersions/Component box Bottom.0012.ipt
Engineering Notebook/Brandon Boyle-Fagan/SD boxes/OldVersions/Component box top.0004.ipt
Engineering Notebook/Brandon Boyle-Fagan/SD boxes/OldVersions/chair power plate.0001.ipt
Engineering Notebook/Brandon Boyle-Fagan/SD boxes/OldVersions/compnent box front L.0001.ipt
Engineering Notebook/Brandon Boyle-Fagan/SD boxes/OldVersions/compnent box front R.0001.ipt
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

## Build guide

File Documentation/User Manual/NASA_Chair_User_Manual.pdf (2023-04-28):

# User Manual for

# NASA Vestibular Chair System

TABLE OF CONTENT

## Contents

USER MANUAL DOCUMENT

### 1 INTRODUCTION

This manual is to be used in conjunction with the NASA Vestibular Chair as well as its external controller interface for proper use and safety measures. This manual will go over how the components are supplied with power, as well as how to supply them with power correctly. Along with that, this manual will explain the proper way to utilize the chair and its controller, as well as some general safety precautions to follow during use and testing.

### 1.1 Powering the NASA Vestibular Chair

The NASA Vestibular Chair is powered by a power supply rated at 24 DC volts with a maximum amperage of 25 amps, however, this upper limit is not reached due to being higher than needed for the components. This power supply is stored within the external controller, and it supplies power to the chair using an ethernet cord from the controller module.

### 1.2 Powering the external controller for the NASA Vestibular Chair

The external controller for the NASA Vestibular Chair is powered by an external computing device via a USB port, connecting the internal electronics to a computer. A computer with the specifications of 2 USB type-A ports, 4GB Ram, Bluetooth compatibility, runs Windows 10 OS at a minimum, or any other up-to-date OS is required to effectively utilize the external controller for the NASA Vestibular Chair. This is due to the programs that the controller is configured with meeting those specifications as of the creation of this user manual.

### 1.3 Powering the patient-held remote for NASA Vestibular Chair testing

The remote used by the patient is powered by a simple battery pack in the base of the controller. These batteries are replaceable, meaning they can be changed in the occurrence of a loss of power

### 2 USES OF HARDWARE

### 2.1 Interface of controller module for the NASA Vestibular Chair

1. “Confirm” button: Confirms the value set by the potentiometer, as well as starting the test and confirming the end of the test.
2. “Arm/Disarm” button: Arms the testing parameters, allowing the test to be executed. Must start in disarm position before the test can be armed.
3. “Back” button: Moves backward through the setting of parameters. (E.g., after confirming rotation speed and moving to setting the duration, back will allow change of rotation speed again.)
4. “Stop” button: Stops the test via software during execution.
5. “Emergency Stop” button: Stops the power supplied to the chair electrically.

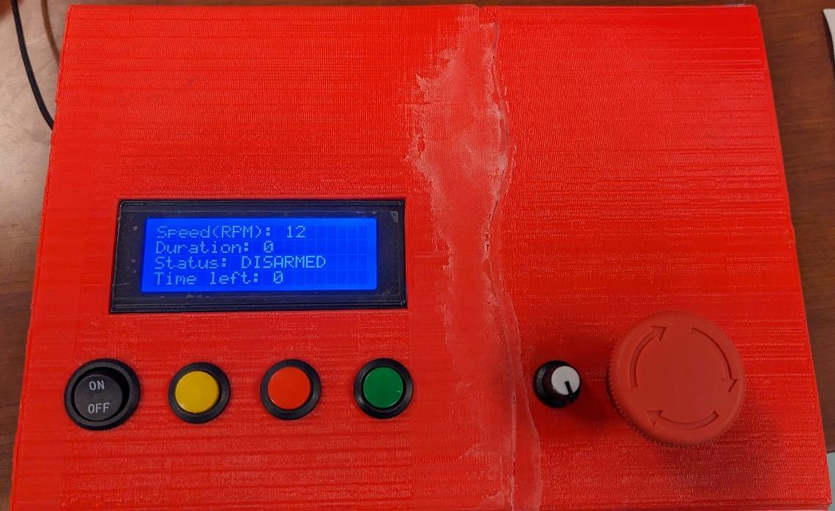
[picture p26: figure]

### 2.2 Use of the NASA Vestibular Chair external controller for testing

1. First, plug the ethernet cable leading from the NASA Vestibular Chair into the controller module, along with plugging in the power supply.
2. Next, plug the USB cord from the controller module into the host PC to be used for data collection.
3. Using the potentiometer knob, set the speed of rotation for the chair to ramp up during the duration of the test.
4. Press the confirm button to set this speed.
5. Using the potentiometer knob, set the duration of the test for the chair. Press the confirm button to set this time.
6. Flip the arm/disarm switch to the armed position, and press the confirm button to start the test.
7. After the test has finished executing, press the confirm button to save the data file to the host PC.

### 2.3 Interface of patient remote for the NASA Vestibular Chair

1. “Left” button: Indicates the user believes they are spinning to the left.
2. “Right” button: Indicates the user believes they are spinning to the right.
3. “On/Off” button: Turns the remote on and off.

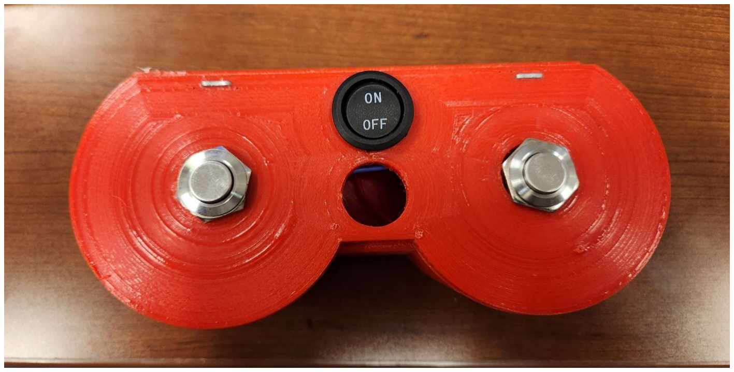
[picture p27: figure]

### 2.4 Uses of NASA Vestibular Chair patient held remote

1. First, turn on the patient remote. Confirm that the remote has paired to the PC/Controller.
2. Next, after beginning the test, the user will either press the left button, the right button, neither, or both to indicate which direction they believe they are spinning.
3. After the duration of the test has been completed, turn the controller off.

### 3 SAFETY

Human input will be necessary for the system as the input for the chair is needed to increase its voltage and by extension its speed. This interaction will cause the user to be able to adjust the chair’s speed gradually through the controller and web interface, meaning there are potential safety concerns if the hardware is used improperly.

### 3.1 Safety when interacting with the NASA Vestibular Chair

The NASA Vestibular Chair will be operating at a relatively high speed compared to the ground it sits on, meaning individuals must stay outside of its spin radius to avoid injury during operation. The chair should also be either bolted down or placed on an elevated platform, as to stop it from tipping over during operation as this has the potential to harm individuals who are sitting in the chair during operation. The system has built-in protection from too much power being sent to the chair, as this would cause too high of a rotational velocity; however, if too much power happens to be applied, there are multiple emergency stop buttons placed in the external controller to remove power from the chair and ease its descent in speed.

3.2 Safety when interacting with the NASA Vestibular Chair external controller.

The external controller is built with an emergency button used to stop power flow to the chair immediately if there are any prevalent issues with its use. This component is activated by applying pressure to the button until it clicks into place. When the button is not in the “open” position, power is allowed to freely flow to the chair. Fans are built into the external controller to control the temperature flow to avoid overheating; however, if there are noticed heating issues, the controller should be turned off for a few moments to regulate its temperature.

### 4 DATA LOGGING APPLICATION

### 4.1 Utilizing the application

1. Turn on the host computer and log in.

### 2. On the desktop locate the “HAL Logger X” folder

3. Plug in the USB cable of the controller module.
4. Locate and start the “serial_logger.exe” application.

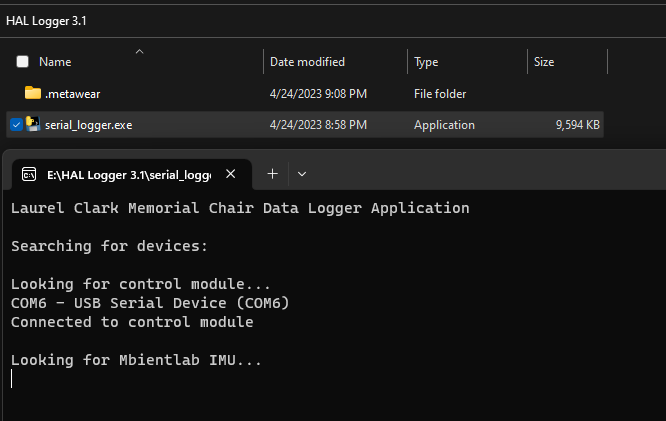
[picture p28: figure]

5. Place the MbientLab IMU within 1ft of the host application.
6. Wait for the connection status to appear.
7. Once the connection status has appeared, set the speed and time using the controller module.
8. Turn on the patient remote and wait for a confirmed signal.

### 9. Once confirmed, arm the control module

10. Press the confirmation button.

### 4.2 Troubleshooting

If an error or software exception occurs in the following steps the trial should be stopped immediately. This is to prevent any harm done to the participants in the trial, the patient sitting in the chair, and or the proctor nearby conducting the test. An example of a software exception that has occurred throughout testing can be found below. The following steps should be taken before continuing the trials:

1. Escort the patient out of the chair.
2. Close the data logging application.
3. Unplug the USB cable from the controller module.

### 4. Repeat the steps from item 4.2 – Starting the application

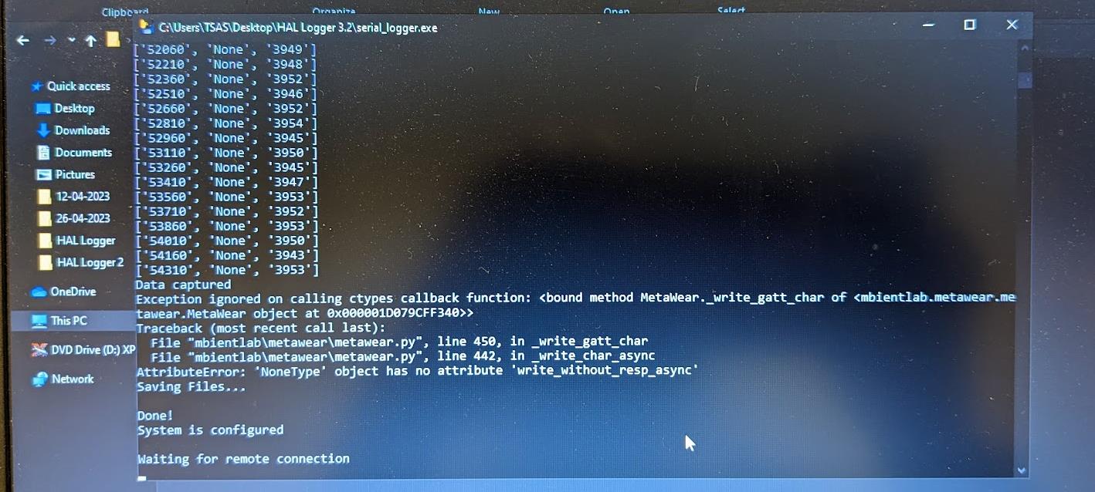
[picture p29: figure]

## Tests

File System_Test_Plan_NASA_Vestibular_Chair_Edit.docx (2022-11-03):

System Test Plan

For

NASA Vestibular Chair

Team members:

Brandon Boyle-Fagan

Matthaeus Gebauer

Miles Osborne

Dylan Prothro

Noah Reid

Kent Wilson

Version/Author | Date
1 | 10-25-22
1.1 | 11-2-22

# Table of Contents

# 1. Introduction

## Purpose

This document is a test plan for NASA Vestibular Chair System Testing, produced by the System Testing team. It describes the testing strategy and approach to testing the team will use to verify that the application meets the established requirements of the product owner.

## Objectives

- Meets the requirements, and specifications set by the product owner.
- Satisfies the needed safety requirements.
- Performs within expected measures with little error.

# 2. Functional Scope

The Modules in the scope of testing for the NASA Vestibular Chair System Testing are mentioned in the document attached in the following path:

1. The System Requirements Specification document: https://github.com/prowl107/NASA-Vestibular-Chair/blob/54404698a9813828192d3e3bc8d47806a4e6bff6/Documentation/SRS/SRS%20V1.md
2. Section 3.1 of this document
3. Standard Operating Procedures for Proctors and Operators
  a. NOTE: This document is planned to be included with the system. Upon completion of its official release, a link will be provided here.

# 3. Overall Strategy and Approach

## Testing Strategy

The NASA Vestibular Chair testing strategy will include testing the functionality of all items included in section 2. Tested items include the following:

1. Transmitting commands to the motor controller to test the functionality of the chair in relation to its rotational speed.
2. Mechanical kill switch operation to ensure power delivery is immediately suspended
3. Soft switches to ensure chair slows down gradually but not abruptly causing damage to the patient
4. Nominal test sequence to raise the motor to a speed within 100 degrees per second and allow the chair to free coast down to an idle state
5. Bi-directional input (i.e., joystick) to allow the user to indicate perceived spin direction

### Function Testing

Test Objective: Ensure the controller module is able to properly provide power to the chair, as well as stop it with its kill switch. This includes both the soft switches and the mechanical kill switch

Technique:

#### Mechanical Hard/Kill Switch Testing:

  1. 1. Wire the controller module to the vestibular chair and initiate a sequence that will provide voltage to rotate the chair
  1. 2. During the test, press/depress the mechanical hard kill switch and measure the input voltage on the chair’s power terminals
  1. 3. Observe the motor behavior of the chair to ensure it is in a free coast state.

#### Soft Switch Testing:

2. 1. Wire the controller module to the vestibular chair and initiate a sequence that will provide voltage to rotate the chair
2. 2. During the test, press/depress the one of the soft kill switches and measure the input voltage on the chair’s power terminals.
2. 3. Observe the motor behavior of the chair to ensure that it reaches 0 rpm in the specified amount of time.

Completion Criteria: In all test cases the controller can provide power to the chair to have it move, and the kill switch is able to kill power to the chair and or bring it to an idle state.

### Data Testing

Test Objective: Ensure the data that is collected is collected properly, able to be exported in the correct format, and displayable.

Technique:

1. Use the Nucleo development board to store and display program data to the seven segment displays
2. Use a STM32 development board to store and transmit the data taken from the tachometer, accelerometer and joystick to the web interface

Completion Criteria: In all test cases, the proper data collection is displayed, and all measured values are accurate.

### Performance Testing

Test Objective: Ensure the chair is able to ramp up to the specified RPM, coast, and then lower its speed until it stops moving.

Technique: Write test cases using the controller that specify the RPM value and measure with a tachometer to determine if the chair is spinning at the correct speed.

Completion Criteria: In all test cases, the chair reaches the RPM set through the controller and manages to coast to a stop.

## System Testing Entrance Criteria

In order to start system testing, the testing readiness can be classified under usability testing, functional testing, and data testing.

## Testing Types

### Usability Testing

The user interface will be tested for ease of use as well as how accurate it is able to perform the actions specified by the user with relation to the controller itself as well as the Vestibular chair. This is done through testing of the controller, as it is the focal point of user interaction with the rest of the system.

### System Requirements Specification, SYS-4: “The system shall have two "soft" kill switches that will allow the chair to "free coast" down to 0 rpm”

### System Requirements Specification, SYS-5:” The system shall have a "hard" mechanical kill switch that will disable power delivery to the chair

### System Requirements Specification, SYS-21:” The system shall support user input from a bi-directional control interface.”

### System Requirements Specification, SYS-26:” The proctor shall only be able to actuate the chair or start a test after a unique button/switch is pressed (arming switch)

### System Requirements Specification, SYS-28:” The web interface shall allow the operator to add different test sequences.”

### System Requirements Specification, SYS-33:” The web interface shall display stored test sequences from a dropdown menu.”

### Data Testing

### The data will be tested for correctness of measurement based on known inputs, as well as its ability to display properly on the display that will be a part of the controller.

### System Requirements Specification, SYS-9:” The system shall record chairs current position (steady state).”

### System Requirements Specification, SYS-10:” The system shall record the desired rpm set by the proctor.”

### System Requirements Specification, SYS-11:” The system shall record the rpm that the chair is currently spinning at.”

### System Requirements Specification, SYS-12: “The system shall record the time elapsed during the current test sequence.”

### System Requirements Specification, SYS-13:” When the user indicates via the bi-directional control method, the system shall record the total time the user indicates they are spinning.”

### System Requirements Specification, SYS-14:” When the user indicates via the bi-directional control method, the system shall record the direction they think they are spinning in.”

### System Requirements Specification, SYS-17:” The system shall record acceleration data.”

### System Requirements Specification, SYS-18:” The system shall record tachometer data.”

### System Requirements Specification, SYS-19:” The system shall record the current direction of the chair”

### Functional Testing

The functionality of the device will be tested for the chair’s ability to function correctly as intended and indicated by the user. This includes its ability to spin in the correct direction, the speed at which the chair rotates, the controller’s ability to function properly in relation to data collection and its ability to provide correct instructions to the functionality of the chair such as setting its speed and direction of rotation.

### System Requirements Specification, SYS-1:” The system shall allow the chair to spin up to a specified RPM determined by the proctor”.

### System Requirements Specification, SYS-2:” After a specified duration set by the operator/proctor, the chair should enter a free coast state.”

### System Requirements Specification, SYS-8:” The system shall not exceed 100 degrees per second (1 revolution every 3 seconds) at any point during its operation.”

### System Requirements Specification, SYS-24:” The system must interface with a wireless bi-directional controller such as a joystick or button.”

## Suspension Criteria and Resumption Requirements

This section will specify the criteria that will be used to suspend all or a portion of the testing activities on the items associated with this test plan.

### Suspension Criteria

- If the controller causes too large of an output of power to the chair resulting in the motor spinning higher than the specified limit of 100 degrees per second.
- If the mechanical kill switch fails to cut power to the chair while it rotates.

### Resumption Requirements

### Resumption of testing will occur when the mechanical kill switch is wired to correctly kill the power, or when an additional switch is used to perform the same function given a malfunction of the initial switch.

# 4. Execution Plan

## Execution Plan

The test plan for the NASA Vestibular Chair is as follows:

Requirement (From SRS) | Test Case Identifier | Input | Expected Behavior | Pass / Fail
SYS-1: The system shall allow the chair to spin up to a specified RPM determined by the proctor | 1.1 | The proctor inputs specified RPM for the chair to spin at. | The chair spins at the RPM determined by the proctor without much deviation.
SYS-4: The system shall have a "soft" kill switch that will allow the chair to "free coast" down to 0 rpm. | 2.1 | The proctor presses the soft kill switch present in the software. | The chair will slow to a stop faster than it would if the speed was manually turned down.
SYS-5: The system shall have a mechanical kill switch that will bring the chair to stop faster than the soft switch. | 3.1 | The proctor presses the mechanical kill switch on the controller. | The chair will slow to a stop faster than the soft kill switch.
SYS-9: The system shall record chairs current position (steady state). | 4.1 | | The chair’s rotational position will be output to the proctor.
SYS-11: The system shall record the rpm that the chair is currently spinning at. | 5.1 | Tachometer readings transmitted to the controller. | The chair’s rotational speed will be output to the proctor.
SYS-15: When the user indicates via the bi-directional control method, the system shall record timestamps of when the button is triggered | 6.1 | The patient moves the joystick in a left or right direction. | The joystick reading will be output to the proctor indicating when it is used.
SYS-21: The system shall support user input from a bi-directional control interface | 7.1 | Presence of a joystick that interfaces with the controller. | The joystick transmits to the controller properly.
SYS-26: The proctor shall only be able to actuate the chair or start a test after a unique button/switch is pressed (arming switch) | 8.1 | Proctor utilizes interface to select a test sequence or input parameters. | The chair will begin moving according to the parameters set by the proctor.
SYS-24: The system must interface with a wireless bi-directional controller such as a joystick or button. | 9.1 | Presence of a joystick that interfaces with the controller. | The joystick interfaces with the controller correctly.
SYS-28: The web interface shall allow the operator to add different test sequences | 10.1 | Proctor inputs parameters into web interface. | Different test sequences are stored in the web interface.
SYS-30: The web interface shall feature a unique button to select the test sequence | 11.1 | Proctor selects saved test sequence. | The selected test sequence is loaded properly.

# 5. Traceability Matrix & Defect Tracking

## Traceability Matrix

List of requirements, corresponding test cases

Requirement CRITICAL: System Requirements Specification, SYS-1: “The system shall allow the chair to spin up to a specified RPM determined by the proctor.”

Test Cases: Check for accurate RPM of the chair with a tachometer compared to proctor set value.

Requirement CRITICAL: System Requirements Specification, SYS-4: “The system shall have a "soft" kill switch that will allow the chair to "free coast" down to 0 rpm.”

Test Cases: Check that the kill switch cuts power to the chair and lets it free spin.

Requirement CRITICAL: System Requirements Specification, SYS-5: “The system shall have a mechanical kill switch that will bring the chair to stop faster than the soft switch.”

Test Cases: Check that the kill switch cuts power to the chair immediately.

Requirement MEDIUM: System Requirements Specification, SYS-9: “The system shall record chair’s current position (steady state).”

Test Cases: Check that the sensors correctly measure the chair’s position.

Requirement MEDIUM: System Requirements Specification, SYS-11: “The system shall record the rpm that the chair is currently spinning at.”

Test Cases: Check for RPM measurement output using tachometer.

Requirement MEDIUM: System Requirements Specification, SYS-15: “When the user indicates via the bi-directional control method, the system shall record timestamps of when the button is triggered.”

Test Cases: Check that joystick transmits properly to controller.

Requirement CRITICAL: System Requirements Specification, SYS-21: “The system shall support user input from a bi-directional control interface.”

Test Cases:

Requirement CRITICAL: System Requirements Specification, SYS-24: “The system must interface with a wireless bi-directional controller such as a joystick or button.”

Test Cases:

Requirement MEDIUM: System Requirements Specification, SYS-28: “The web interface shall allow the operator to add different test sequences.”

Test Cases: Check that the operator is allowed to utilize multiple test cases.

Requirement MEDIUM: System Requirements Specification, SYS-30: “The web interface shall feature a unique button to select the test sequence.”

Test Cases: Check that the software defined button will connect to the correct sequence.

## Defect Severity Definitions

Critical | The defect causes a catastrophic or severe error that results in major problems and the functionality rendered is unavailable to the user. A manual procedure cannot be either implemented or a high effort is required to remedy the defect. Examples of a critical defect are as follows: - System abends - RPM limit is exceeded - Data is corrupted or cannot post to the database
Medium | The defect does not seriously impair system function can be categorized as a medium Defect. A manual procedure requiring medium effort can be implemented to remedy the defect. Examples of a medium defect are as follows: - Form navigation is incorrect - Field labels are not consistent with global terminology
Low | The defect is cosmetic or has little to no impact on system functionality. A manual procedure requiring low effort can be implemented to remedy the defect. Examples of a low defect are as follows: - Repositioning of fields on screens - Text font on reports is incorrect

# 6. Environment

## Environment

- In order to conduct the testing, the tester needs to have the following:
  1. Access to the NASA Vestibular chair
  2. Access to the controller of the chair
  3. Access to the selected power supply or equivalent

# 7. Assumptions

This section details specific assumptions that are made throughout the project

- There is no individual sitting in the NASA Vestibular Chair
- The power supply connected to the controller and chair does not output higher than 24V

# 8. Risks and Contingencies

Some risks involved with testing the NASA Vestibular Chair involve the possibility of spinning the chair too fast. This consideration is made because if the controller supplies to high of a voltage, the chair could risk falling over or hurting the individual sitting in it. The contingency in place to prevent this is code built into the controller to prevent the voltage from being supplied at a value that would cause the rotational speed of the chair to exceed 100 degrees per second, as well as a mechanical kill switch that will be built into the controller to shut off power to the chair if it begins to spin too fast.

Another potential risk involved with the testing comes in the form of loss of information between the controller and analog components of the chair. Since the components within the NASA Vestibular Chair are mostly analog, there is a chance of loss of data between the components present in the internal hardware and those in the controller. A contingency for this is the inclusion of digital components within the controller, to have two forms of communication with the internal hardware of the chair as a backup in case one fails.

Risk # | Risk | Impact | Contingency
1 | Chair Spins too Fast | High | Code built into the controller to prevent the voltage from being supplied at a value that would cause the rotational speed of the chair to exceed 100 degrees per second, as well as a mechanical kill switch that will be built into the controller to shut off power to the chair if it begins to spin too fast
2 | Information loss between controller and chair | High | Inclusion of digital components within the controller, to have two forms of communication with the internal hardware of the chair as a backup in case one fails

# 9. Appendices

None currently available

CBC Projects System Test Plan Version 1.0

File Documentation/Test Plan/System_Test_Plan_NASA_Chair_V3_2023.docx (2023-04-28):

System Test Plan

For

NASA Vestibular Chair

Team members:

Brandon Boyle-Fagan

Matthaeus Gebauer

Miles Osborne

Dylan Prothro

Noah Reid

Kent Wilson

Version/Author | Date
1 | 10-25-22
1.1 | 11-2-22
1.2 | 12-7-22
2.1 | 2-18-23
2.2 | 3-7-23
3.0 | 4-11-23
3.1 | 4-14-23

# Table of Contents

# 1. Introduction

## Purpose

This document is a test plan for the NASA Vestibular Chair System, produced by the system testing team. It describes the testing strategy and approach to testing the team will use to verify that the application meets the established requirements of the product owner.

## Objectives

- Meets the requirements, and specifications set by the product owner.
- Satisfies the needed safety requirements.
- Performs within expected measures with little error.

# 2. Functional Scope

The Modules in the scope of testing for the NASA Vestibular Chair System testing are mentioned in the document attached in the following path:

1. The System Requirements Specification document: https://github.com/prowl107/NASA-Vestibular-Chair/blob/main/Documentation/SRS/System%20Requirements%20Specification%20V2.pdf

NOTE: Version 3 of the SRS is currently in development and the link will be updated to reflect the changes upon completion.

2. Section 3.1 of this document
3. Standard Operating Procedures for Proctors and Operators:

https://github.com/prowl107/NASA-Vestibular-Chair/blob/main/Documentation/User%20Manual/NASAChair_User_Manual.pdf

# 3. Overall Strategy and Approach

## Testing Strategy

The NASA Vestibular Chair testing strategy will include testing the functionality of all items included in section 2. Tested items include the following:

1. Transmitting commands to the motor controller to test the functionality of the chair in relation to its rotational speed (e.g., increase the voltage sent to the chair by a rate of 0.05V per second, decrease the voltage sent to the chair by a rate of 0.05V per second.)
2. Mechanical kill switch operation to ensure power delivery is immediately suspended.
3. Soft switches to ensure the chair slows down gradually but not abruptly causing damage to the patient (e.g., removing power at a rate of 0.05V per second)
4. Nominal test sequence to raise the motor to a speed within 100 degrees per second and allow the chair to free coast down to an idle state
5. Bi-directional input (buttons) to allow the user to indicate the perceived spin direction to the system as either “left”, “right”, “both”, or none.

### Function Testing

Test Objective: Ensure the controller module can properly provide power to the chair, as well as stop it with its kill switch. This includes both the soft switches and the mechanical kill switch.

#### Mechanical Hard/Kill Switch Testing:

  1. 1. Wire the controller module to the vestibular chair and initiate a sequence that will provide voltage to rotate the chair.
  1. 2. During the test, press/depress the mechanical hard kill switch and measure the input voltage on the chair’s power terminals.
  1. 3. Observe the motor behavior of the chair to ensure it is in a free coast state.

#### Soft Switch Testing:

2. 1. Wire the controller module to the vestibular chair and initiate a sequence that will provide voltage to rotate the chair.
2. 2. During the test, press/depress the soft kill switch and measure the input voltage on the chair’s power terminals.
2. 3. Observe the motor behavior of the chair to ensure that it reaches 0 rpm in the specified amount of time.

Completion Criteria: In all test cases the controller can provide power to the chair to have it move, and the kill switch can kill power to the chair and or bring it to an idle state.

### Data Testing

Test Objective: Ensure the data that is collected is collected properly, able to be exported in the correct format, and displayable.

Technique:

1. Start the web interface
2. Initialize the control module as the receiver and the patient remote control as the sender.
3. Wait for an established connection to be made before proceeding.
4. Begin data transmission from the remote to the control module.
5. The control module will receive and store all packets from the receiver.
6. The control module will send the collected data to the web interface.
7. The web interface shall display the data collected from the receiver.

Completion Criteria: In all test cases, the proper data collection is displayed, and all measured values are accurate.

### Performance Testing

Test Objective: Ensure the chair can ramp up to the specified RPM, coast, and then lower its speed until it stops moving.

Technique: Write test cases using the controller module that specifies the RPM value and measures with a tachometer to determine if the chair is spinning at the correct speed.

Completion Criteria: In all test cases, the chair reaches the RPM set through the controller and manages to coast to a stop.

## System Testing Entrance Criteria

In order to start system testing, the testing readiness can be classified under usability testing, functional testing, and data testing.

## Testing Types

### Usability Testing

The user interface will be tested for ease of use as well as how accurately it is able to perform the actions specified by the user in relation to the controller itself as well as the vestibular chair. This is done through stress testing of the controller, as it is the focal point of user interaction with the rest of the system.

### System Requirements Specification, SYS-5:” The system shall have a "hard" mechanical kill switch that will disable power delivery to the chair.

### System Requirements Specification, SYS-20:” The system shall support user input from a bi-directional control interface.”

### System Requirements Specification, SYS-25:” The proctor shall only be able to actuate the chair or start a test after a unique button/switch is pressed (arming switch)

### System Requirements Specification, SYS-30:” The web interface shall allow the operator to add different test sequences.”

### System Requirements Specification, SYS-58:” The web interface shall display stored test sequences from a dropdown menu.”

### Data Testing

### The data will be tested for the correctness of measurement based on known inputs, as well as its ability to display properly on the display that will be a part of the controller module. Additionally, this presents criteria to evaluate the functionality of the patient's remote device.

### System Requirements Specification, SYS-8:” The system shall record the chair's current position (steady state).”

### System Requirements Specification, SYS-9:” The system shall record the desired rpm set by the proctor.”

### System Requirements Specification, SYS-10:” The system shall record the rpm that the chair is currently spinning at.”

### System Requirements Specification, SYS-11: “The system shall record the time elapsed during the current test sequence.”

### System Requirements Specification, SYS-12:” When the user indicates via the bi-directional control method, the system shall record the total time the user indicates they are spinning.”

### System Requirements Specification, SYS-13:” When the user indicates via the bi-directional control method, the system shall record the direction they think they are spinning in.”

### System Requirements Specification, SYS-16:” The system shall record acceleration data.”

### System Requirements Specification, SYS-17:” The system shall record tachometer data.”

### System Requirements Specification, SYS-68:” The system shall record the time when the chair comes to a complete stop after the trial duration has elapsed.”

### System Requirements Specification, SYS-69:” The system shall continue to record data until the proctor has signaled the end of the test.”

### Functional Testing

The functionality of the device will be tested for the chair’s ability to function correctly as intended and indicated by the user. This includes its ability to spin at a speed, the proctor defines, the controller’s ability to function properly in relation to data collection, and its ability to provide correct instructions for the functionality of the chair such as setting its speed and direction of rotation.

### System Requirements Specification, SYS-1:” The system shall allow the chair to spin up to a specified RPM determined by the proctor”.

### System Requirements Specification, SYS-2:” After a specified duration set by the operator/proctor, the chair should enter a free coast state.”

### System Requirements Specification, SYS-4:” The system shall not exceed 100 degrees per second (1 revolution every 3 seconds) at any point during its operation.”

### System Requirements Specification, SYS-23:” The system must interface with a wireless bi-directional controller such as a joystick or button.”

### System Requirements Specification, SYS-70:” The control module shall maintain wireless communication with the patient remote throughout the entirety of each trial.”

## Suspension Criteria and Resumption Requirements

This section will specify the criteria that will be used to suspend all or a portion of the testing activities on the items associated with this test plan.

### Suspension Criteria

- If the controller causes too large of an output of power to the chair resulting in the motor spinning higher than the specified limit of 100 degrees per second.
- If the mechanical kill switch fails to cut power to the chair while it rotates.
- Non-deterministic transitions between system states

### Resumption Requirements

### Resumption of testing will occur when the mechanical kill switch is wired to correctly kill the power, or when an additional switch is used to perform the same function given a malfunction of the initial switch.

# 4. Execution Plan

## Execution Plan

The test plan for the NASA Vestibular Chair is as follows:

Requirement (From SRS) | Test Case Identifier | Input | Expected Behavior | Pass / Fail
SYS-1: The system shall allow the chair to spin up to a specified RPM determined by the proctor | 1.1 | The proctor inputs specified RPM for the chair to spin at. | The chair spins at the RPM determined by the proctor without much deviation. | Pass*
SYS-24: The proctor shall be able to stop the currently executing test by pressing the “soft kill switch” | 2.1 | 1. The proctor presses the soft kill switch during a currently running test before the target RPM is reached. 2. The proctor pressed the soft kill switch after the target RPM has been reached. | The chair will slow to a stop faster than it would if the speed was manually turned down. | Pass
SYS-51: The proctor shall be able to terminate power delivery to the chair by pressing a mechanical switch | 3.1 | The proctor presses the mechanical kill switch on the controller. | The chair will enter a free coast state and gradually slow down to 0 RPM. The control module should remain powered | Pass
SYS-8: The system shall record the chair’s current position (steady state). | 4.1 | 1. The target RPM for the test 2. Measurements of the chair’s current speed with timestamps | The chair’s rotational position will be displayed to the proctor. | Pass
SYS-10: The system shall record the rpm that the chair is currently spinning. | 5.1 | Tachometer readings collected from the chair | 1. The chair’s rotational speed will be output to the proctor. 2. The chair’s rotational speed will be stored temporarily in a non-volatile storage location. | Pass
SYS-12: When the user indicates via the bi-directional control method, the system shall record the total time the user indicated they are spinning | 6.1 | 1. Continuous signals of the patient interacting with the wireless joystick regardless of the direction 2. Timestamps of each signal sent to the control module | 1. The joystick reading will be output to the proctor indicating when it is used. 2. The chair’s rotational speed will be stored temporarily in a non-volatile storage location | Pass
SYS-20: The system shall support user input from a bi-directional human input device | 7.1 | Presence of a joystick that interfaces with the controller. | The joystick transmits to the controller properly. | Pass
SYS-21: The system shall allow the user to indicate what direction they are spinning via a bi-directional control method | 7.2 | Presence of a joystick that interfaces with the controller | The user’s feedback from the input device will be displayed accurately after the test has been completed | Pass
SYS-22: The system shall record intermediate values for the direction indicated | 7.3 | Presence of a joystick that interfaces with the controller | The chair’s rotational speed will be stored temporarily in a non-volatile storage location | Pass
SYS-23: The system shall interface with a wireless bi-directional human input device such as a joystick or button | 7.4 | Presence of a joystick that interfaces with the controller. | The joystick interfaces with the controller correctly. | Pass
SYS-27: The proctor shall set the duration of the test either via the web interface or the controller module | 8.1 | Proctor utilizes an interface to select a test sequence or input parameters. | The chair will begin moving according to the parameters set by the proctor. | Pass
SYS-15: The system shall have the ability to export data in a human-readable format | 9.1 | Collection of sample data from a running or test or randomly generated data in an equivalent format | 1. The processed data will be displayed to the user via the web interface 2. From the web interface, the proctor can export the data in a CSV file format 3. The generated file is viewable without any abnormalities | Pass
SYS-19: The system shall record data at a sample rate of at least 20 HZ | 10.1 | 1. Collection of sample data from a running or test or randomly generated data from a HITL sequence. 2. All data will have a timestamp associated | Visual inspection of data and the respective timestamp will demonstrate that there are at least 20 samples taken per second. | Pass
SYS-33: The web interface shall not execute any commands unless connection with the control module has been established | 11.1 | A hardware connection between the control module and host PC (wire, serial-to-USB adapter, etc.) | The web waits for an acknowledgment from the control module before allowing any test or commands to be executed | Currently under test
SYS-30: The web interface shall allow the operator to add different test sequences | 12.1 | Proctor inputs parameters into web interface. | Different test sequences are stored in the web interface. | (Deprecated)
HDW-11: The physical switch shall not disconnect power to the control module | 13.1 | A test setup consisting of a DC power supply wired to the motor controller, vestibular chair, and control module, with the physical switch to toggle power | 1. Once the mechanical switch is pressed/depressed, the power should be disconnected. The chair should stop moving 2. The control module should still be powered which can be verified by observing the onboard LEDs | Pass
SYS-28: The proctor shall only be able to actuate the chair or start a test after a unique button/switch is pressed (arming switch) | 15.1 | 1. A connection was established between the host PC and the controller module 2. Control module setup integrated with the vestibular chair | 1. While the proctor is configuring the test, there will be no movement from the chair 2. The on-screen button for starting the test will be disabled until the arming switch has been enabled | Pass

NOTE: The test for SYS-1 does pass. However, it is based on speeds when a load is not applied to the chair. However, the product owner is aware of the behavior and feels that the current output will suffice. Once the desired speed has been reached, it does not deviate from the target.

NOTE: The test for SYS-10 does pass. The value is recorded with the analog value from the tachometer with a 12-bit resolution such that 0° corresponds to a value of 0 and 360° corresponds to 4095.

NOTE: The test for SYS-30 is marked as deprecated. After discussions with our shareholders, it was determined that this feature is no longer needed and consequently the exclusion of the test. The listing will remain in the test plan for record keeping.

# 5. Traceability Matrix & Defect Tracking

## Traceability Matrix

List of requirements, corresponding test cases

Requirement CRITICAL: System Requirements Specification, SYS-1: “The system shall allow the chair to spin up to a specified RPM determined by the proctor.”

Test Cases: Check for accurate RPM of the chair with a tachometer compared to proctor set value.

Requirement CRITICAL: System Requirements Specification, SYS-43: “If the controller detects a soft kill switch was pressed, the controller shall bring the chair to a speed of 0 RPM at a gradual rate.”

Test Cases: Check that the kill switch cuts power to the chair and lets it free spin.

Requirement CRITICAL: System Requirements Specification, SYS-51: “The proctor shall be able to terminate power delivery to the chair by pressing a mechanical switch.”

Test Cases: Check that the kill switch cuts power to the chair immediately.

Requirement MEDIUM: System Requirements Specification, SYS-8: “The system shall record chair’s current position (steady state).”

Test Cases: Check that the sensors correctly measure the chair’s position.

Requirement MEDIUM: System Requirements Specification, SYS-10: “The system shall record the rpm that the chair is currently spinning at.”

Test Cases: Check for RPM measurement output using tachometer.

Requirement MEDIUM: System Requirements Specification, SYS-14: “When the user indicates via the bi-directional control method, the system shall record timestamps of when the button is triggered.”

Test Cases: Check that buttons on the handheld controller transmits properly to controller module.

Requirement CRITICAL: System Requirements Specification, SYS-20: “The system shall support user input from a bi-directional control interface.”

Test Cases:

Requirement CRITICAL: System Requirements Specification, SYS-23: “The system must interface with a wireless bi-directional controller such as a joystick or button.”

Test Cases:

Requirement MEDIUM: System Requirements Specification, SYS-30: “The web interface shall allow the operator to add different test sequences.”

Test Cases: Check that the operator is allowed to utilize multiple test cases.

Requirement MEDIUM: System Requirements Specification, SYS-55: “The web interface shall feature a unique button to select the test sequence.”

Test Cases: Check that the software defined button will connect to the correct sequence.

## Defect Severity Definitions

Critical | The defect causes a catastrophic or severe error that results in major problems and the functionality rendered is unavailable to the user. A manual procedure cannot be either implemented or a high effort is required to remedy the defect. Examples of a critical defect are as follows: - System abends - RPM limit is exceeded - Data is corrupted or cannot post to the database
Medium | A defect that does not seriously impair system function can be categorized as a medium Defect. A manual procedure requiring medium effort can be implemented to remedy the defect. Examples of a medium defect are as follows: - Form navigation is incorrect - Field labels are not consistent with global terminology
Low | The defect is cosmetic or has little to no impact on system functionality. A manual procedure requiring low effort can be implemented to remedy the defect. Examples of a low defect are as follows: - Repositioning of fields on screens - The text font on reports is incorrect

# 6. Environment

## Environment

- To conduct the testing, the tester needs to have the following:
  1. Access to the NASA Vestibular chair
  2. Access to the controller of the chair
  3. Access to the selected power supply or equivalent
  4. Access to the patient remote device

# 7. Assumptions

This section details specific assumptions that are made throughout the project

- No individual is sitting in the NASA Vestibular Chair
- The power supply connected to the controller and chair does not output higher than 12V

# 8. Risks and Contingencies

Some risks involved with testing the NASA Vestibular Chair involve the possibility of spinning the chair too fast. This consideration is made because if the controller supplies too high of a voltage, the chair could risk falling over or hurting the individual sitting in it. The contingency in place to prevent this is the code built into the controller to prevent the voltage from being supplied at a value that would cause the rotational speed of the chair to exceed 100 degrees per second, as well as a mechanical kill switch that will be built into the controller to shut off power to the chair if it begins to spin too fast.

Another potential risk involved with the testing comes in the form of loss of information between the controller and analog components of the chair. Since the components within the NASA Vestibular Chair are mostly analog, there is a chance of loss of data between the components present in the internal hardware and those in the controller. A contingency for this is the inclusion of digital components within the controller, to have two forms of communication with the internal hardware of the chair as a backup in case one fails.

Risk # | Risk | Impact | Contingency
1 | Chair Spins too Fast | High | Code built into the controller to prevent the voltage from being supplied at a value that would cause the rotational speed of the chair to exceed 100 degrees per second, as well as a mechanical kill switch which will be built into the controller to shut off power to the chair if it begins to spin too fast UPDATE: From testing, it was observed that the chair could be physically stopped by holding it in place in the event of an emergency
2 | Information loss between controller and chair | High | Inclusion of digital components within the controller, to have two forms of communication with the internal hardware of the chair as a backup in case one fails

# 9. Appendices

None currently available

CBC Projects System Test Plan Version 1.0

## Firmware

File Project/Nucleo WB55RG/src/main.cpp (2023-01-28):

/**********************************************************************************
* File: main.cpp
*
* Purpose: Application entry point
**********************************************************************************/
#include "chair_lib_gbl.h"
#include "chair_pins.h"
#include <LiquidCrystal_I2C.h> // includes the LiquidCrystal Library 
#include <RadioHead.h>
#include <RH_ASK.h>
#include <SPI.h>
#include <Wire.h>

/* Peripherals */
LiquidCrystal_I2C lcd(0x27, 20, 4);
FSM fsm;
SMC smc; /* Simple motor controller */
RH_ASK receiver; /* Wireless transmitter/receiver */

void setup() {
Serial.begin(115200);
/*************************************************************************
* Local Variables
*************************************************************************/ 

/* Test sequence duration */
long test_start_time;                                     
long test_target_time;
long test_time_elapsed;
int32_t time_left;
uint8_t counter;

/* Finite State Machine (FSM) parameters */
SYS_STATES_T state_index;

/* Motor controller target parameters */
int16_t current_speed; 
int16_t speed_target;
float speed_target_percent = 0.0;
uint32_t rpm_encoder_val = 0;
uint32_t rpm_encoder_prev_state = analogRead(A0);
uint32_t rpm_encoder_new_state;
int32_t speed_target_scaled;

/* Wireless Communication parameters */
/*************************************************************************
* Expected Messages: 
* No button                   0
* Left button:                1
* Right button:               2
* Both button:                3
* Patient emergency button:   4
*************************************************************************/
char msg[5];
uint8_t msg_len = 6;
String data_log[5]; 
uint8_t msg_index = 0;

// /*************************************************************************
// * Initialize Local Variables
// *************************************************************************/ 
smc = SMC(RPM_POTENTIOMETER);
counter = 0;
fsm = FSM(SYS_INIT);
test_start_time = 0;  
test_target_time = 0;
test_time_elapsed = 0;
state_index = SYS_INIT;
current_speed = 0;
speed_target = 0;

if (!receiver.init())
Serial.println("init failed");

/*************************************************************************
* Start system Operation:
*
* States:
* 1 - SYS_INIT
* 2 - PROCTOR_OP_RPM 
* 3 - PROCTOR_OP_TIME
* 4 - SYS_ARM_HOLD
* 5 - ARMED_OPERATION
* 6 - ARMED_TARGET_REACHED
**************************************************************************/
while(1){
switch (fsm.getCurrentState())
{
case SYS_INIT:
  Serial.println("NASA Vestibular Chair -- Loading interface...");
  // Wire.begin(); 
  // Wire.setClock(400000);

  /* Initialize I/O Pins */
  sys_io_init();

  /* Initialize motor controller & interface */
  smc.exitSafeStart();

  /* Initialize displays */
  sys_display_init(&lcd);

  /* Initialize web interface */

  /* Transition to PROCTOR_OP_RPM */
  state_index = PROCTOR_OP_RPM;
  break;

case PROCTOR_OP_RPM:

  /***********************************************************************
  * Retrieve target speed from analog input
  ***********************************************************************/ 
  speed_target = smc.controlPot(); /* NOTE: pass rpm_encoder target to smc.setMotorSpeed() during operation*/
  speed_target_percent = (speed_target/3200.0)*100; 
  speed_target_scaled = round((0.015833333333333335 * speed_target) - 8.916666666666671);
    //   Serial.print("speed_target_scaled: ");
    // Serial.println(speed_target_scaled);
  if(speed_target_scaled < 12)
  {
    speed_target_scaled = 12;
  }

  if(speed_target_scaled > 16)
  {
    speed_target_scaled = 16;
  }

  lcd.setCursor(strlen("Speed(RPM): "), 0);
  lcd.print(speed_target_scaled,10);

  /* Clear trailing digit from display if less than 1000*/
  if(speed_target_scaled<1000)
  {
    lcd.setCursor(15, 0);
    lcd.print(' ');
  }

  if(speed_target_scaled<100)
  {
    lcd.setCursor(14, 0);
    lcd.print(' ');
  }

  if (speed_target_scaled<10)
  {
    lcd.setCursor(13,0);
    lcd.print(' ');
  }

  if (digitalRead(CONFIRMATION_BTN) == LOW)
  {
    /* Wait until button depress */
    while(digitalRead(CONFIRMATION_BTN) == LOW);
    state_index = PROCTOR_OP_TIME;
  }

  break;

case PROCTOR_OP_TIME: 
  /***********************************************************************
  * Retrieve target duration from analog input
  ***********************************************************************/ 
  test_target_time = map(smc.controlPot(), 0, 3200, 0, 120); /* NOTE: pass rpm_encoder target to smc.setMotorSpeed() during operation*/

  lcd.setCursor(strlen("Duration: "), 1);
  lcd.print(test_target_time,10);

  /* Clear trailing digit from display if less than 1000*/
  if(test_target_time<100)
  {
    lcd.setCursor(12, 1);
    lcd.print(' ');
    if(test_target_time < 10)
    {
    lcd.setCursor(11, 1);
    lcd.print(' ');
    }
  }

  if (digitalRead(CONFIRMATION_BTN) == LOW && digitalRead(REJECT_BTN) == HIGH)
  {
    /* Wait until button depress */
    while(digitalRead(CONFIRMATION_BTN) == LOW);
    state_index = SYS_ARM_HOLD;
  }else if(digitalRead(CONFIRMATION_BTN) == HIGH && digitalRead(REJECT_BTN) == LOW) /* Return to previous state */
  {
    /* Wait until button depress */
    while(digitalRead(REJECT_BTN) == LOW);
    state_index = PROCTOR_OP_RPM;
  }

  // Serial.print("\tTime: ");
  // Serial.print("speed_target_scaled: ");
  // Serial.println(test_target_time);
  break;

case SYS_ARM_HOLD:
  lcd.setCursor(strlen("Status: "), 2);
  /* Return to previous state */
  if (digitalRead(REJECT_BTN) == LOW)
  {
    lcd.print("        ");
    lcd.setCursor(strlen("Status: "), 2);
    lcd.print("DISARMED");
    state_index = PROCTOR_OP_TIME;    
    /* Wait until button depress */
    while(digitalRead(REJECT_BTN) == LOW);
    break;
  }

  /* Wait until button/switch confirmation before allowing operation */
  if (digitalRead(ARMING_SWITCH_1) == HIGH)
  {
    lcd.print("        ");
    lcd.setCursor(strlen("Status: "), 2);
    lcd.print("DISARMED");
    state_index = SYS_ARM_HOLD;
    digitalWrite(DISARMED_LED, HIGH);
    digitalWrite(ARMED_LED, LOW);
    break;

  }else if(digitalRead(ARMING_SWITCH_1) == LOW){
    lcd.print("        ");
    lcd.setCursor(strlen("Status: "), 2);
    lcd.print("ARMED");
    digitalWrite(DISARMED_LED, LOW);
    digitalWrite(ARMED_LED, HIGH);
  
   if(digitalRead(CONFIRMATION_BTN) == LOW) {
    lcd.print("       ");
    lcd.setCursor(strlen("Status: "), 2);
    /* Wait until button depress */
    while(digitalRead(CONFIRMATION_BTN) == LOW);
    state_index = ARMED_OPERATION;
    lcd.print("ARMED_OP");
  }
  }

  break;

case ARMED_OPERATION:
  test_start_time = millis();
  test_time_elapsed = millis();
  test_target_time = test_target_time*1000; /* Convertfrom S to MS */

  lcd.setCursor(0,3);
  lcd.print("Time left: ");

 while(state_index == ARMED_OPERATION)
 {
  /*********************************************************************
  * Emergency Stop Detected --> Stop Test Immediately
  **********************************************************************/
  if(digitalRead(ESTOP_BTN) == LOW  || strstr(msg, "STOP") )
  {
    emergency_stop();
    Serial.println("EOF");
    memset(msg, '\0', 6);
    state_index = SYS_INIT;
    break;
  }

  /**********************************************************************
  * Capture patient data from wireless device
  * and send to PC
  * 
  * @TODO: Send data to PC! (pyserial)
  **********************************************************************/
  if (receiver.recv(msg, &msg_len)) // Non-blocking
  {
  int i;
  // *msg = 0;multi_btn_signalp
  // Serial.println("DATA_LOG:");
  Serial.print((test_time_elapsed - test_start_time));
  // delay(500);
  Serial.print(",");
  // delay(500);
  Serial.println((char*)msg);
  }
  // data_log[msg_index] = (test_time_elapsed - test_start_time) + "," + (char*)msg;
  // Serial.println(data_log[msg_index]);


  /******************************multi_btn_signalp***************************************
  * Gradually increase RPM until target is reached
  **********************************************************************/
  if(test_target_time+1000 > (test_time_elapsed - test_start_time))
  {
    if(current_speed < speed_target)
    {
    smc.setMotorSpeed(current_speed);
    current_speed+=2;
    // state_index = ARMED_TARGET_REACHED;
    }else{
      smc.setMotorSpeed(current_speed);
      // state_index = ARMED_TARGET_REACHED;
    }
    test_time_elapsed = millis();
  /* Print Time left on last line of the LCD: */
  lcd.setCursor(strlen("Time left: 0")-1, 3);
  time_left = ((test_target_time - (test_time_elapsed - test_start_time))/1000);
  lcd.print(time_left);  
  }

  if(time_left<100)
  {
    lcd.setCursor(13, 3);
    lcd.print(' ');
    if(time_left<10){
      lcd.print(' ');
     lcd.setCursor(12, 3);
     lcd.print(' ');
    }
  }

  /*********************************************************************
  * If set duration is reached move to ARNED_TARGET_REACHED state
  **********************************************************************/
  if(time_left <= 0)
  {
    state_index = ARMED_TARGET_REACHED;
  }
  
  test_time_elapsed = millis();
 }
  break; 

case ARMED_TARGET_REACHED:
  /*********************************************************************
  * Gradually decrease RPM until target is reached
  **********************************************************************/
 lcd.clear();
 lcd.setCursor(0,0);
 lcd.print("Test Complete");
 lcd.setCursor(0,1);
 lcd.print("Slowing down");
    while(current_speed > 0)
    {
    current_speed-=50;
    state_index = ARMED_TARGET_REACHED;
    /**********************************************************************
    * Capture patient data from wireless device
    * and send to PC
    * 
    * @TODO: Send data to PC! (pyserial)
    **********************************************************************/
  if(receiver.recv(msg, &msg_len))
  {
    int i;
  // *msg = 0;
  // Serial.println("DATA_LOG:");
  Serial.print((test_time_elapsed - test_start_time));
  // delay(500);
  Serial.print(",");
  // delay(500);
  Serial.println((char*)msg);
  }
    
    smc.setMotorSpeed(current_speed);
    delay(200);
    }


  /**********************************************************************
  * @todo Finish logging data.
  **********************************************************************/
lcd.setCursor(0,2);
lcd.print("Saving data to file");
/* Insert end of file signal */
Serial.println("EOF");
delay(5000);
lcd.setCursor(0,3);
lcd.print("Done");
delay(3000);

  /**********************************************************************
  * Reset for next sequence
  **********************************************************************/
 sys_display_init(&lcd);
 *msg = 0;
 state_index = SYS_INIT;

  break;

case INVALID:
  /* Do Nothing */
  break;

default:
  break;
}

/*************************************************************************
* Update FSM
*************************************************************************/
// Serial.print("Current State index: ");
// Serial.print(fsm.getCurrentState());
// Serial.print("\t");
// Serial.print("Next state index: ");
// Serial.println(state_index);
fsm.setCurrentState(state_index);
delay(25); 
}

for(;;);
}

void loop(){} /* Do Nothing */
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

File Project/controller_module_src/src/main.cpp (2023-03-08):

/**********************************************************************************
* File: main.cpp
*
* Purpose: Application entry point
**********************************************************************************/
#include "chair_lib_gbl.h"
#include "chair_pins.h"
#include <LiquidCrystal_I2C.h> // includes the LiquidCrystal Library 
#include <RadioHead.h>
#include <RH_ASK.h>
#include <SPI.h>
#include <Wire.h>

/* Peripherals */
LiquidCrystal_I2C lcd(0x27, 20, 4);
FSM fsm(SYS_INIT);
SMC smc(A1); /* Simple motor controller */
RH_ASK receiver; /* Wireless transmitter/receiver */
uint8_t start_test_flag;

void setup() {
Serial.begin(115200);
/*************************************************************************
* Local Variables
*************************************************************************/ 

/* Test sequence duration */
long test_start_time;                                     
long test_target_time;
long test_time_elapsed;
int32_t time_left;
start_test_flag = 0;
long chair_stop_timestamp;
long end_of_test_timestamp;
uint8_t chair_stop_flag;

/* Finite State Machine (FSM) parameters */
SYS_STATES_T state_index;

/* Motor controller target parameters */
int16_t current_speed; 
int16_t speed_target;
float speed_target_percent = 0.0;
int32_t speed_target_scaled;

/* Wireless Communication parameters */
/*************************************************************************
* Expected Messages: 
* No button                   0
* Left button:                1
* Right button:               2
* Both button:                3
* Patient emergency button:   4
*************************************************************************/
char msg[6];
uint8_t msg_len = 6;

// /*************************************************************************
// * Initialize Local Variables
// *************************************************************************/ 
smc = SMC(RPM_POTENTIOMETER);
fsm = FSM(SYS_INIT);
test_start_time = 0;  
test_target_time = 0;
test_time_elapsed = 0;
state_index = SYS_INIT;
current_speed = 0;
speed_target = 0;
chair_stop_timestamp = 0;
end_of_test_timestamp = 0;
chair_stop_flag = 0;

/*************************************************************************
* Start system Operation:
*
* States:
* 1 - SYS_INIT
* 2 - PROCTOR_OP_RPM 
* 3 - PROCTOR_OP_TIME
* 4 - SYS_ARM_HOLD
* 5 - ARMED_OPERATION
* 6 - ARMED_TARGET_REACHED
**************************************************************************/
// sys_display_init(&lcd);
// while(true){
//   Serial.println(smc.controlPot());
//   delay(500);
// }

while(1){
switch (fsm.getCurrentState())
{
case SYS_INIT:
  Serial.println("NASA Vestibular Chair -- Loading interface...");

  /* Initialize I/O Pins */
  sys_io_init();

  /* Initialize motor controller & interface */
  Wire.begin(); 
  Wire.setClock(400000);
  smc.exitSafeStart();

  /* Initialize displays */
  sys_display_init(&lcd);

  /* Initialize web interface */

  /* Initialize communication interface */
  if (!receiver.init())
  Serial.println("init failed");
  for (uint8_t i = 0; i < sizeof(msg); i++)
  {
    msg[i] = 0;
  }

  /* Transition to PROCTOR_OP_RPM */
  state_index = PROCTOR_OP_RPM;
  break;
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

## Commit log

2022-09-16 Added information regarding power supply to the motor.
2022-10-06 Added SDD
    Began framework for SDD
2022-10-06 Searchable 403D Manual
    Chair manual document written in word to allow it to be searchable
    *note* Is missing the circuit diagrams from Dr. Liu's pdf
2022-12-06 Create motor contorller- arduino.ino.ino
2022-12-10 eng notebook
    [motor values.xlsx]
2023-01-23 tach code update and cad file upload
    [Component box Bottom 1.stl, Component box Bottom 2.stl, Component box Bottom 3.stl, Component box Bottom 4.stl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]
2023-02-22 Updates
    updated eng notebook 1 month... tacometer, 3d files.
    [chair power plate.0001.ipt, chair power plate.ipt, chair power plate.stl, compnent box front L.ipt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]
2023-03-08 tac update
    [paitent remote box.0004.ipt, paitent remote box.0006.ipt, paitent remote box.ipt, paitent remote box.stl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]
2023-04-04 boxes
    updated designs for 3d printed stuffs
    [Component box Bottom.0005.ipt, Component box Bottom.0008.ipt, Component box Bottom.ipt, Component box Bottom.stl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]
2023-04-08 Update eng notebook spring.txt
2023-04-21 box stuff
    [Component box Bottom 1.stl, Component box Bottom 2.stl, Component box Bottom 3.stl, Component box Bottom 4.stl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]
2023-04-24 box again. im scared
    [Component box Bottom 1.stl, Component box Bottom 2.stl, Component box Bottom 3.stl, Component box Bottom 4.stl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]
2023-04-25 more box updates
    [Component box Bottom tall.ipt, Component box top.ipt, compnent box front L.stl, compnent box front R.stl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]
